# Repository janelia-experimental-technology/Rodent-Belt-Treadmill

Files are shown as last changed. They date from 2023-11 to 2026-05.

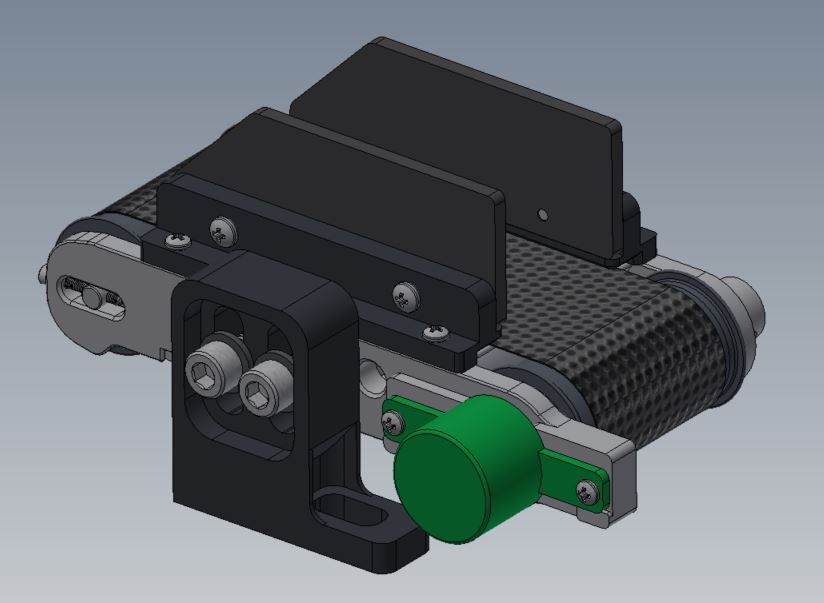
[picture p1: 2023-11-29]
J005558 TREADMILL.JPG

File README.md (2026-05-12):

# Rodent-Belt-Treadmill
Low friction belt treadmill for use in space constrained experimental rigs

Designed at HHMI's Janelia research campus by the jET team, this treadmill is relatively small and inexpensive compared to most existing designs. It is manually driven with an encoder which tracks the movement of the belt. The encoder does not have to be connected, unless it is desired to record or analyze the motion. Encoder interfaces are documented in a separate repository here: https://github.com/janelia-experimental-technology/Treadmill-Interface as the interface may be used with multiple treadmill types.

It may be used for natural action (e.g., walking) for the mouse to take during an experiment instead of standing still. For example, some users let the mice walk normally on the treadmill and then play a tone the mouse associates with a trained response to see if the mouse will start or stop moving.

Advantages: This was designed to fit underneath MIMMS 2P microscopes where space is limited. There are now some commercial options available based on this design, as well as other commercial options.

Interface: These may be placed under an imaging microscope or other behavioral setup with a head-fixed rodent on it. 

Construction: The treadmill is composed of 3D printed parts and two machined axles that can be made by a machine shop on a lathe with simple tooling. There are also some laser cut side walls on the treadmill and a laser cut belt as well. 
The belt is seamed together using a heat sealer such as this one from Amazon: 
8" (200mm) Impulse Manual Bag Sealer Heat Sealer http://a.co/8Zj5Gaq

Teflon tape used to hold the belt halves in position:
http://catalog.cshyde.com/keyword/s-ptfe-teflon-products-ptfe-teflon-tapes-4/skived-high-density-ptfe-tape-with-silicone?key=all&&keyword=R233&SchType=2

See the individual part drawings for more detail on printing and fabricating each parts. See the attached assembly drawing for the BOM including purchased commercial items needed to complete the treadmill. 

Operation: Researchers can physically mount the treadmill and place the mouse on top of it. Some training is required of the mouse. 

Maintenance: The belts need to be cleaned regularly to keep them turning smoothly. Many users have spare belts that they swap between. If there is enough space in your rig other options such as the cylindrical treadmill are good options that do not require as much maintenance. 

Opportunity: Free to make for Non-Profit Research by downloading the design here or on Flintbox. See included hardware license. 

Rights and designs available for Commercial License. Janelia makes no endorsements or guarantees of licensee products.

For inquiries, please contact innovation@janelia.hhmi.org and reference: Janelia 2017-049
https://hhmi.flintbox.com/technologies/5e4af2a5-6154-4bc0-a10d-56b5b6dce978

To cite the designs, please use DOI:  https://doi.org/10.25378/janelia.24691311

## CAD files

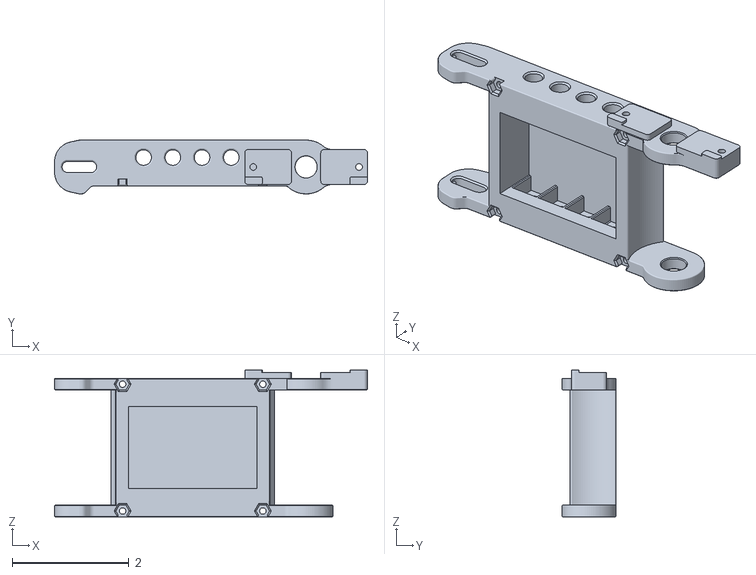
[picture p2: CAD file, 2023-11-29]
Part Models and Drawings/J007811 NRB MAIN BODY INSERTS Rev -.stl
5.35 x 0.922 x 2.51

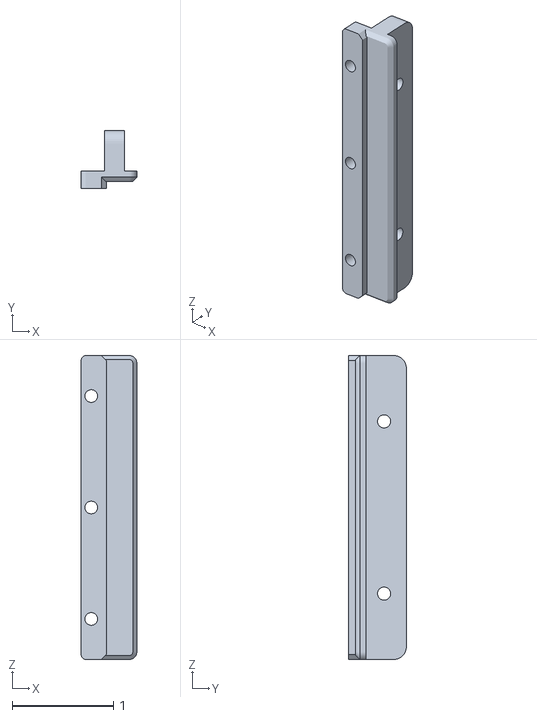
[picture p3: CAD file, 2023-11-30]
Part Models and Drawings/J006163 NRB LOW GUIDE RAIL Rev -.stl
0.55 x 0.57 x 3.00

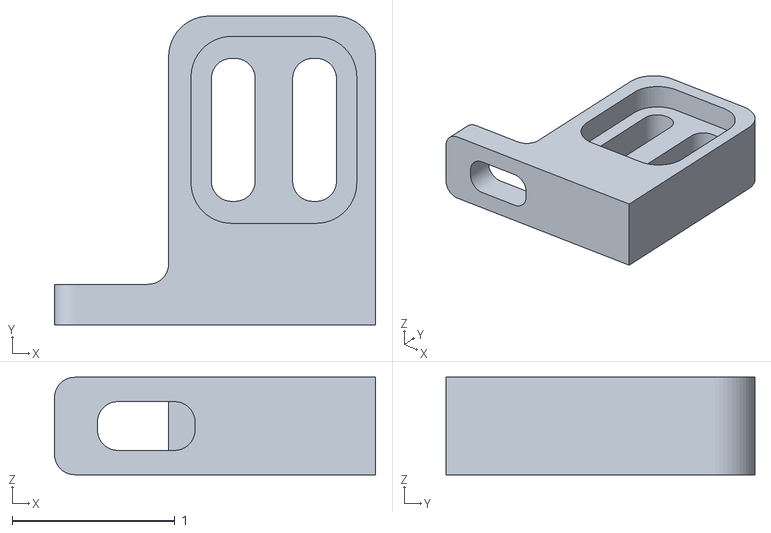
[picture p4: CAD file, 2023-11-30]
Part Models and Drawings/J005557 NRB ADJ BRKT MR Rev -.stl
1.98 x 1.90 x 0.6

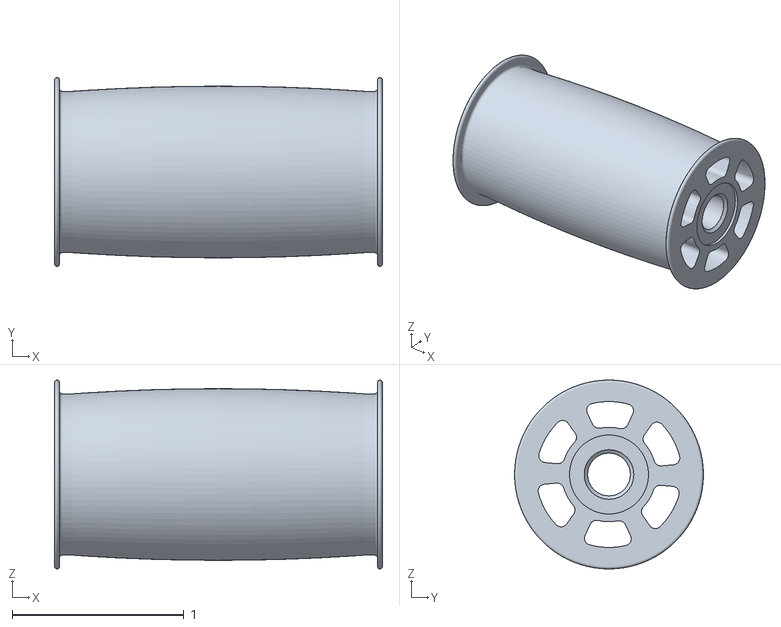
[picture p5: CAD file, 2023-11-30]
Part Models and Drawings/J005553 NRB DRIVE ROLLER Rev -.stl
1.91 x 1.10 x 1.10

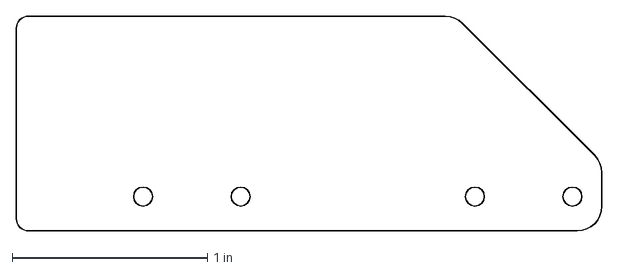
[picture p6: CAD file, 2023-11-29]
Part Models and Drawings/J005548 NRB BRKT SIDE WALL Rev A.dxf
3.00 x 1.10 in

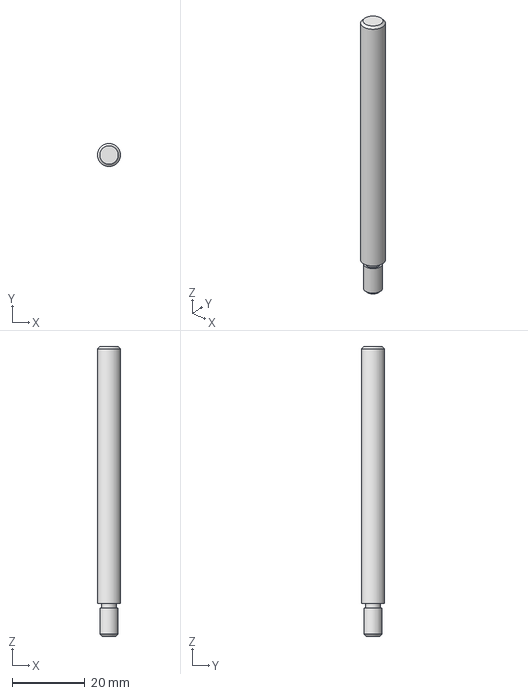
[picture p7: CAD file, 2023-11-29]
Part Models and Drawings/J005526 NRB DRIVE SHAFT Rev A.stp
6.34 x 6.35 x 79.7 mm

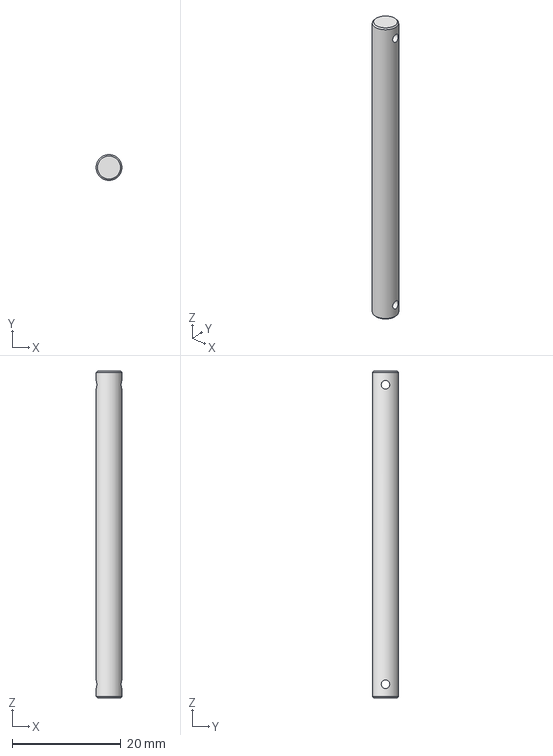
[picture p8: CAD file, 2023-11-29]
Part Models and Drawings/J005527 NRB IDLER SHAFT Rev A.stp
4.75 x 4.75 x 60.2 mm

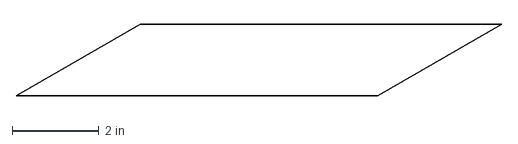
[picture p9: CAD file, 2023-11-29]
Part Models and Drawings/J005559 NRB BELT FLAT PATTERN Rev B.dxf
11.2 x 1.65 in

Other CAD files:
Part Models and Drawings/J005556 NRB ADJ BRKT ML Rev -.stl
Part Models and Drawings/J005551 NRB ROLLER Rev -.stl
Pack and Go Inventor Files/57155K335.ipt
Pack and Go Inventor Files/57155K336.ipt
Pack and Go Inventor Files/90107A126.ipt
Pack and Go Inventor Files/90965A170.ipt
Pack and Go Inventor Files/91828A113_TYPE 18-8 STAINLESS STEEL HEX NUT.ipt
Pack and Go Inventor Files/92000A106.ipt
Pack and Go Inventor Files/92000A112.ipt
Pack and Go Inventor Files/92000A118.ipt
Pack and Go Inventor Files/92196A540.ipt
Pack and Go Inventor Files/92290A746.ipt
Pack and Go Inventor Files/94785A415_TYPE 18-8 STAINLESS STEEL SQUARE NUT.ipt
Pack and Go Inventor Files/98317A214.ipt
Pack and Go Inventor Files/9946K110.ipt
Pack and Go Inventor Files/HEDR-5420-ES214.ipt
Pack and Go Inventor Files/HEDR-5420-ES214_DISC.ipt
Pack and Go Inventor Files/NRB ADJ BRKT ML.ipt
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

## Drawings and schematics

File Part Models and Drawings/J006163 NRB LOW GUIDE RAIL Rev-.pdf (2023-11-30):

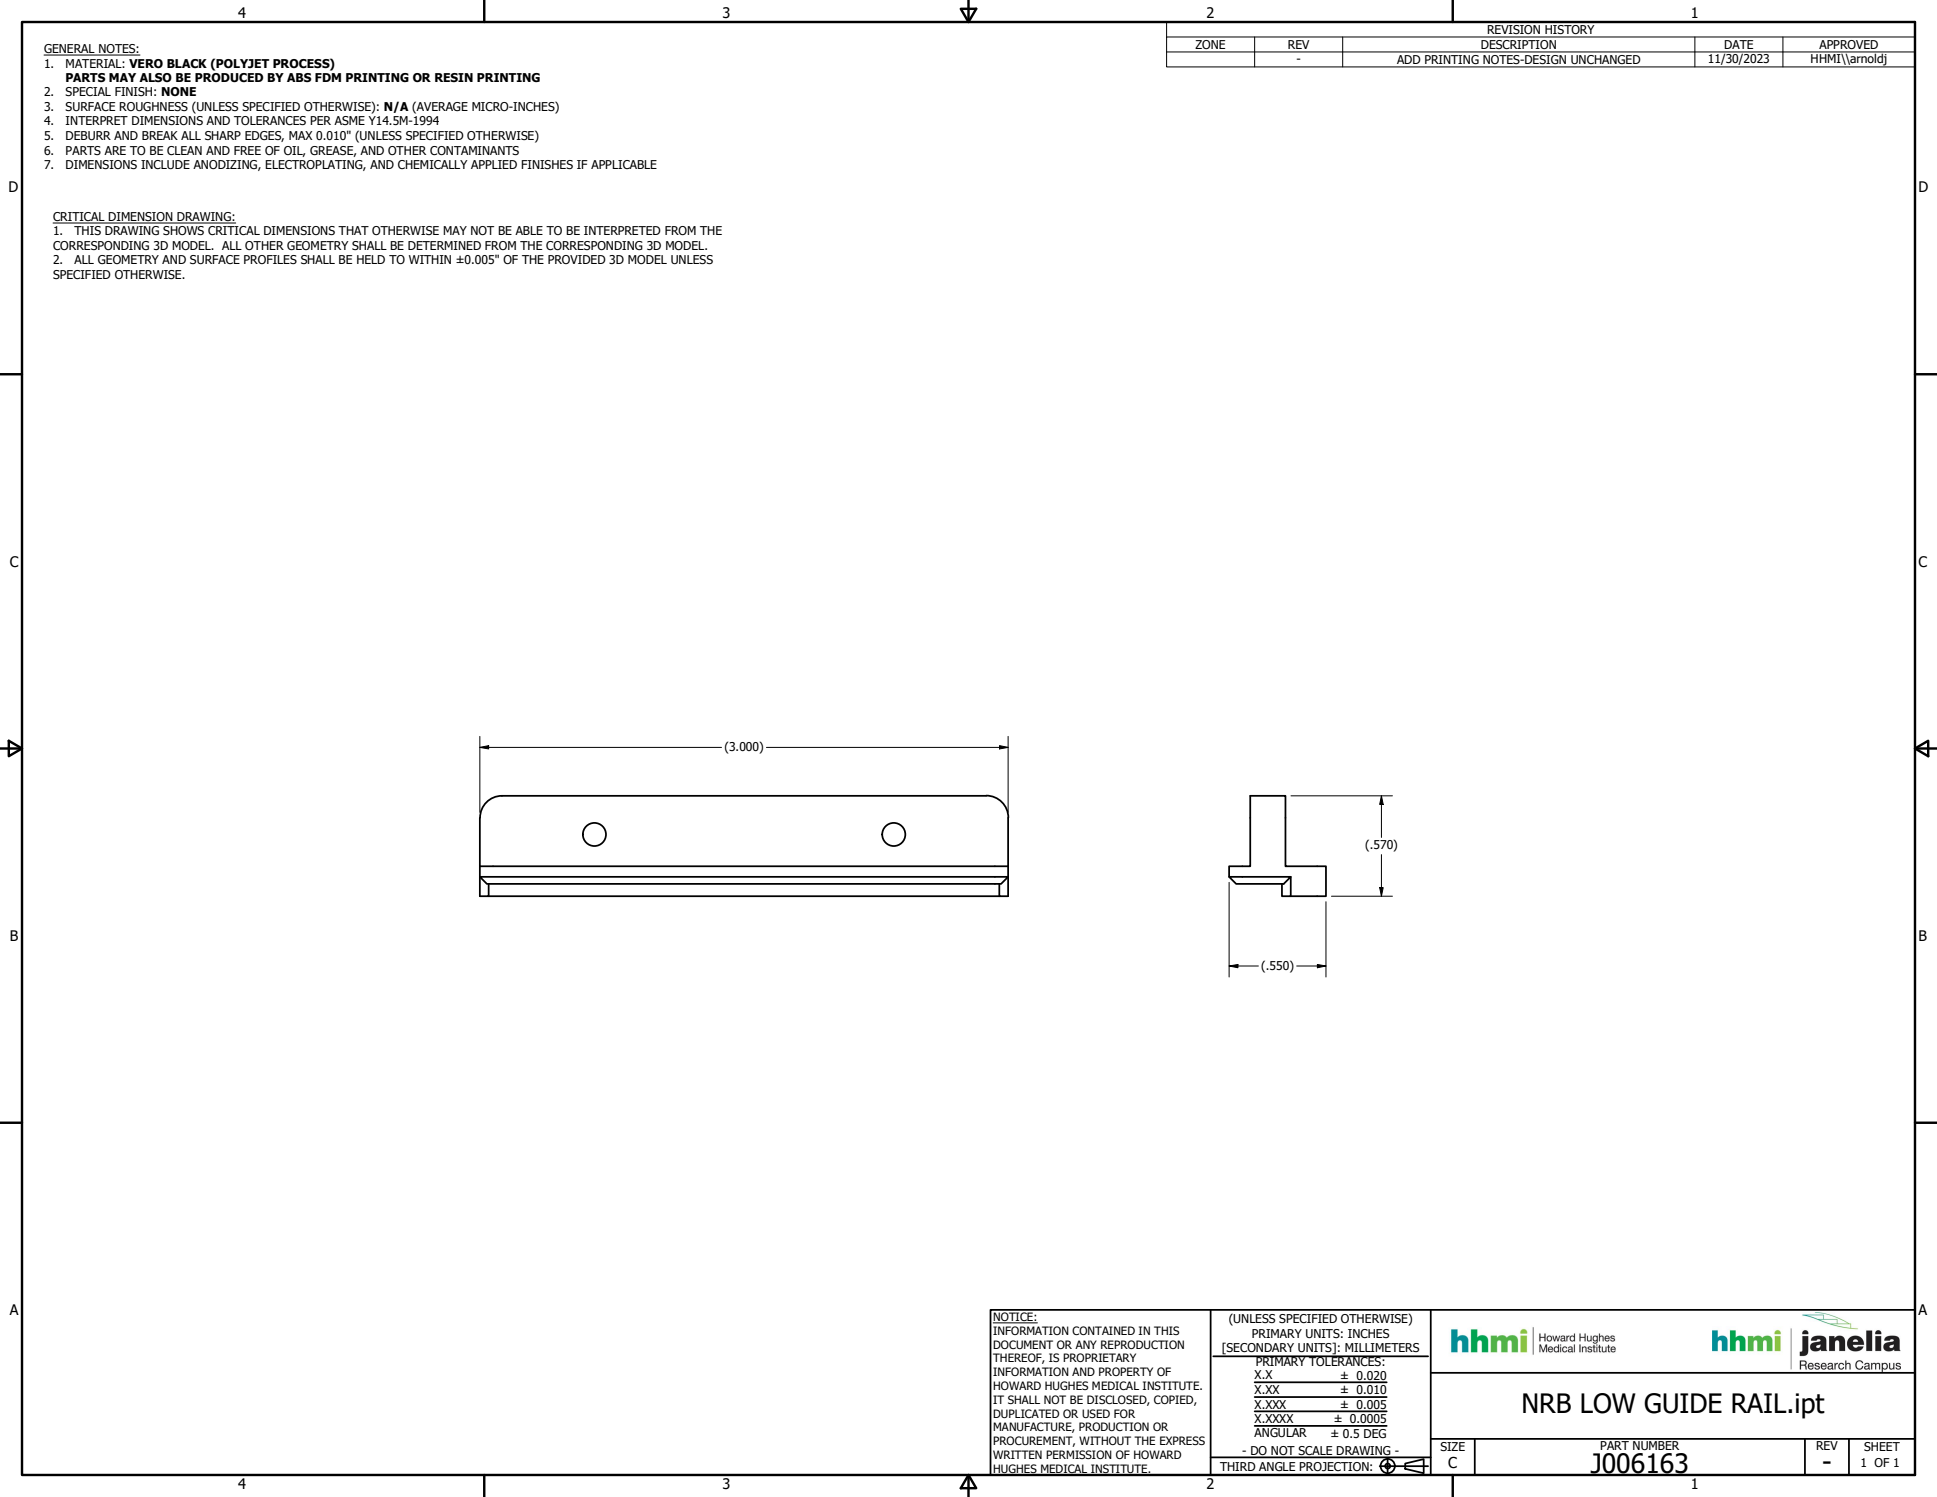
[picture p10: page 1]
PART NUMBER; 1 OF 1 THIRD ANGLE PROJECTION:; ± 0.020 ± 0.010 ± 0.005 ± 0.0005 ± 0.5 DEG; REVISION HISTORY

GENERAL NOTES:
1. MATERIAL: VERO BLACK (POLYJET PROCESS)
PARTS MAY ALSO BE PRODUCED BY ABS FDM PRINTING OR RESIN PRINTING
2. SPECIAL FINISH: NONE
3. SURFACE ROUGHNESS (UNLESS SPECIFIED OTHERWISE): N/A (AVERAGE MICRO-INCHES)
4. INTERPRET DIMENSIONS AND TOLERANCES PER ASME Y14.5M-1994
5. DEBURR AND BREAK ALL SHARP EDGES, MAX 0.010" (UNLESS SPECIFIED OTHERWISE)
6. PARTS ARE TO BE CLEAN AND FREE OF OIL, GREASE, AND OTHER CONTAMINANTS
7. DIMENSIONS INCLUDE ANODIZING, ELECTROPLATING, AND CHEMICALLY APPLIED FINISHES IF APPLICABLE

ZONE | REV | DESCRIPTION | DATE | APPROVED

- | ADD PRINTING NOTES-DESIGN UNCHANGED | 11/30/2023 | HHMI\\arnoldj

CRITICAL DIMENSION DRAWING:
1. THIS DRAWING SHOWS CRITICAL DIMENSIONS THAT OTHERWISE MAY NOT BE ABLE TO BE INTERPRETED FROM THE
CORRESPONDING 3D MODEL. ALL OTHER GEOMETRY SHALL BE DETERMINED FROM THE CORRESPONDING 3D MODEL.
2. ALL GEOMETRY AND SURFACE PROFILES SHALL BE HELD TO WITHIN ±0.005" OF THE PROVIDED 3D MODEL UNLESS
SPECIFIED OTHERWISE.

NOTICE:
INFORMATION CONTAINED IN THIS
DOCUMENT OR ANY REPRODUCTION
THEREOF, IS PROPRIETARY
INFORMATION AND PROPERTY OF
HOWARD HUGHES MEDICAL INSTITUTE.
IT SHALL NOT BE DISCLOSED, COPIED,
DUPLICATED OR USED FOR
MANUFACTURE, PRODUCTION OR
PROCUREMENT, WITHOUT THE EXPRESS
WRITTEN PERMISSION OF HOWARD
HUGHES MEDICAL INSTITUTE.

(UNLESS SPECIFIED OTHERWISE)
PRIMARY UNITS: INCHES
[SECONDARY UNITS]: MILLIMETERS
PRIMARY TOLERANCES:
X.XXX
X.XXXX
ANGULAR
- DO NOT SCALE DRAWING -

NRB LOW GUIDE RAIL.ipt

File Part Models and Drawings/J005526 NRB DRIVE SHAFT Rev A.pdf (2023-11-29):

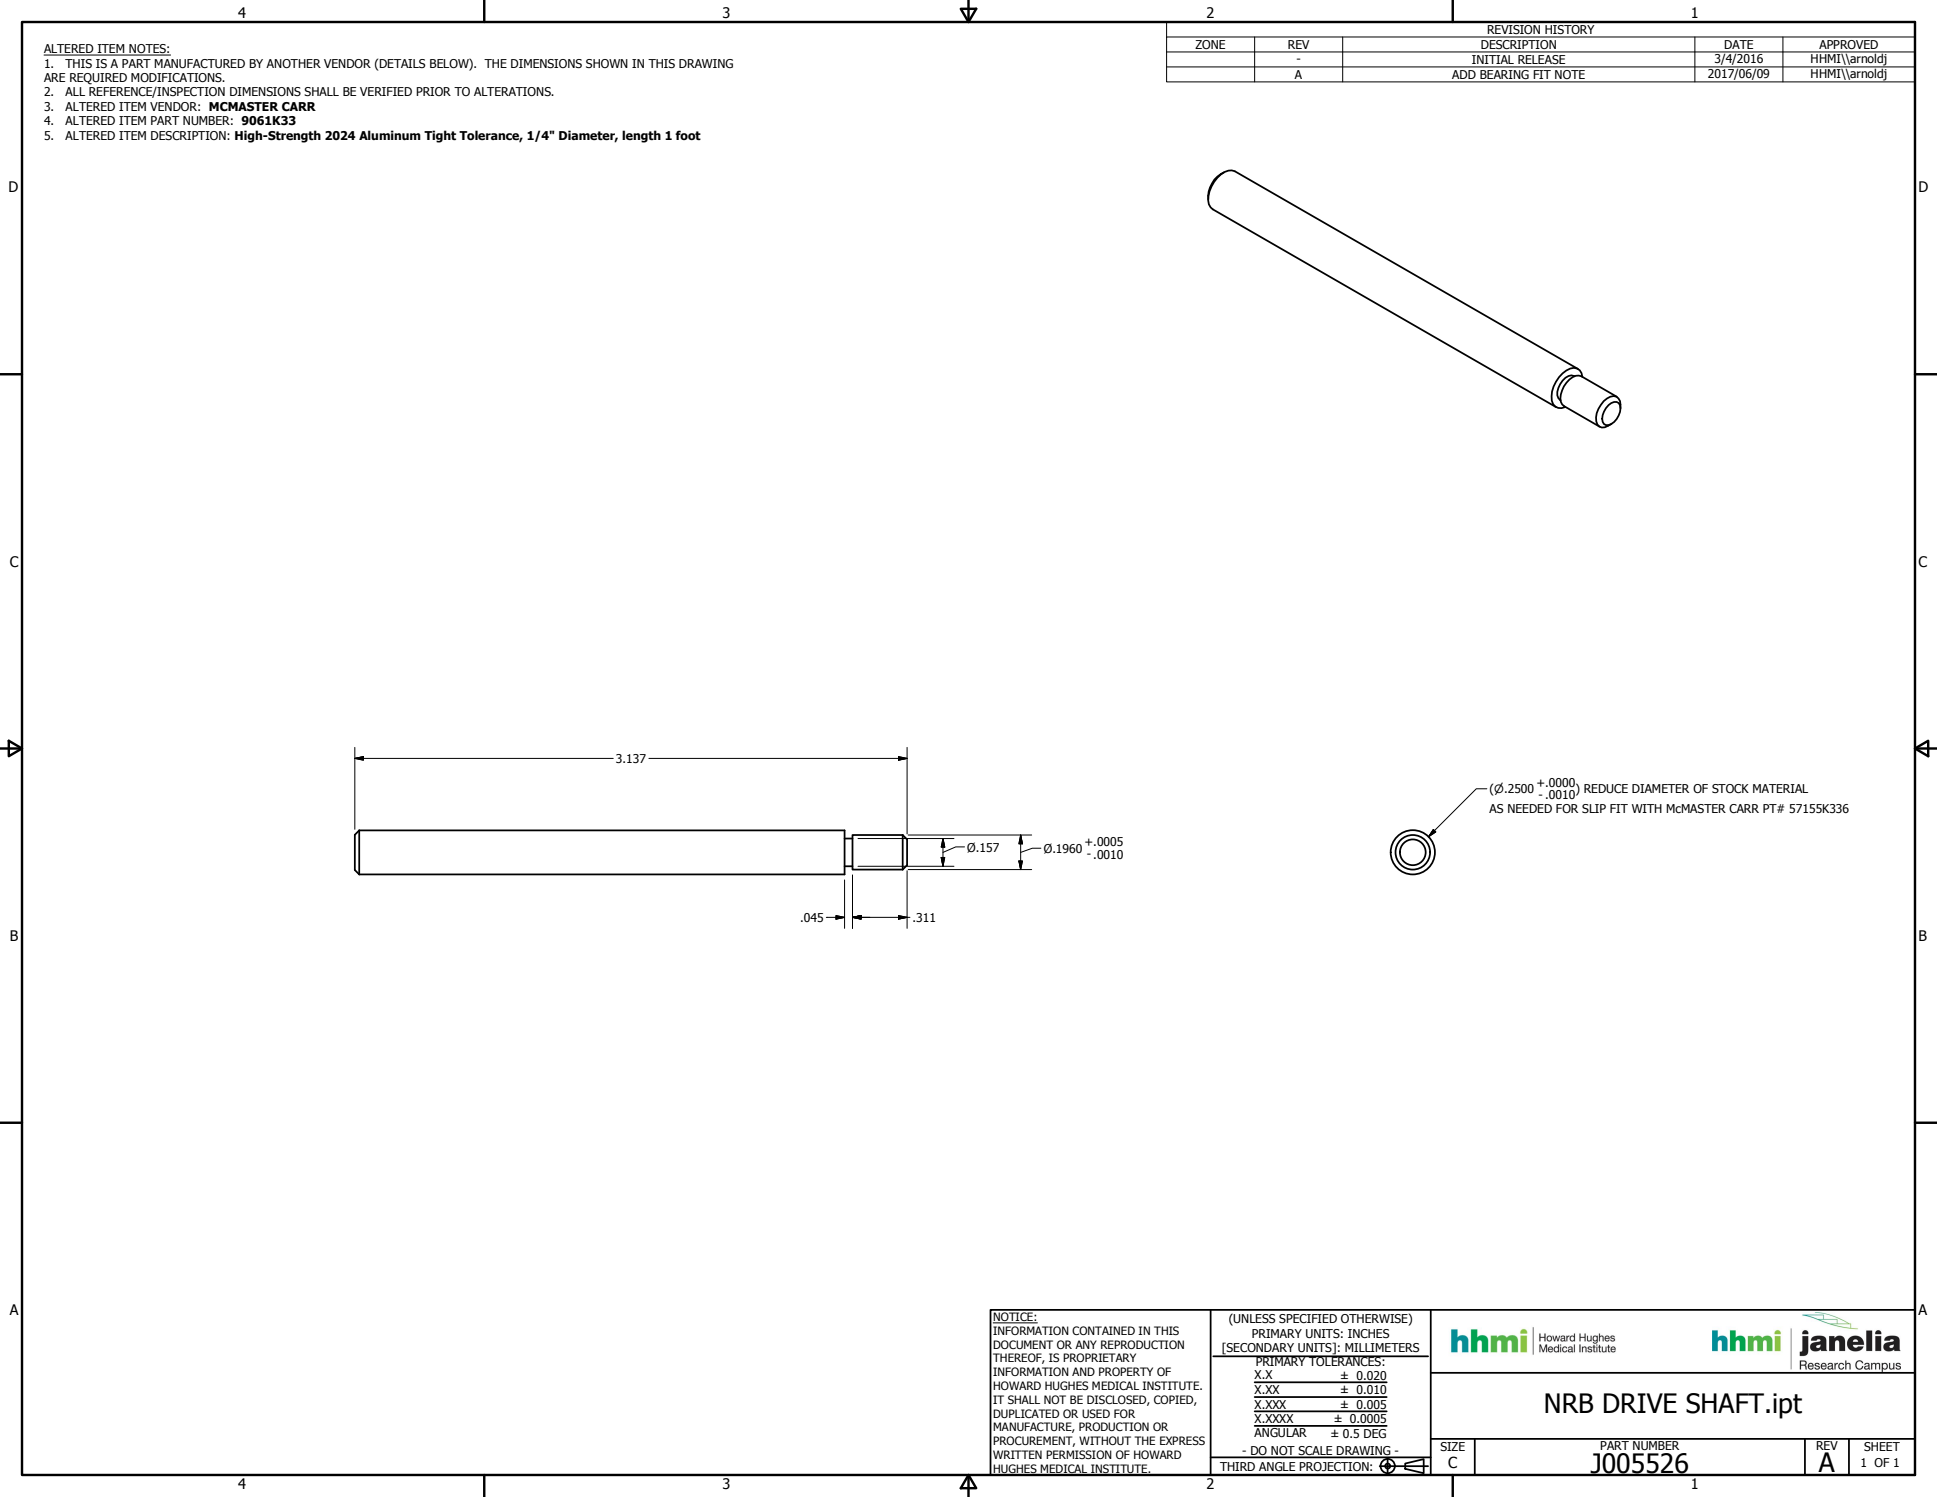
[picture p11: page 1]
PART NUMBER; SIZE; REV; SHEET; 1 OF 1 THIRD ANGLE PROJECTION:; ± 0.020 ± 0.010 ± 0.005 ± 0.0005 ± 0.5 DEG; REVISION HISTORY; ZONE; DESCRIPTION; DATE; APPROVED; INITIAL RELEASE; HHMI\\arnoldj; ADD BEARING FIT NOTE; ) REDUCE DIAMETER OF STOCK MATERIAL

ALTERED ITEM NOTES:
1. THIS IS A PART MANUFACTURED BY ANOTHER VENDOR (DETAILS BELOW). THE DIMENSIONS SHOWN IN THIS DRAWING
ARE REQUIRED MODIFICATIONS.
2. ALL REFERENCE/INSPECTION DIMENSIONS SHALL BE VERIFIED PRIOR TO ALTERATIONS.
3. ALTERED ITEM VENDOR: MCMASTER CARR
4. ALTERED ITEM PART NUMBER: 9061K33
5. ALTERED ITEM DESCRIPTION: High-Strength 2024 Aluminum Tight Tolerance, 1/4" Diameter, length 1 foot

AS NEEDED FOR SLIP FIT WITH McMASTER CARR PT# 57155K336

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

NRB DRIVE SHAFT.ipt

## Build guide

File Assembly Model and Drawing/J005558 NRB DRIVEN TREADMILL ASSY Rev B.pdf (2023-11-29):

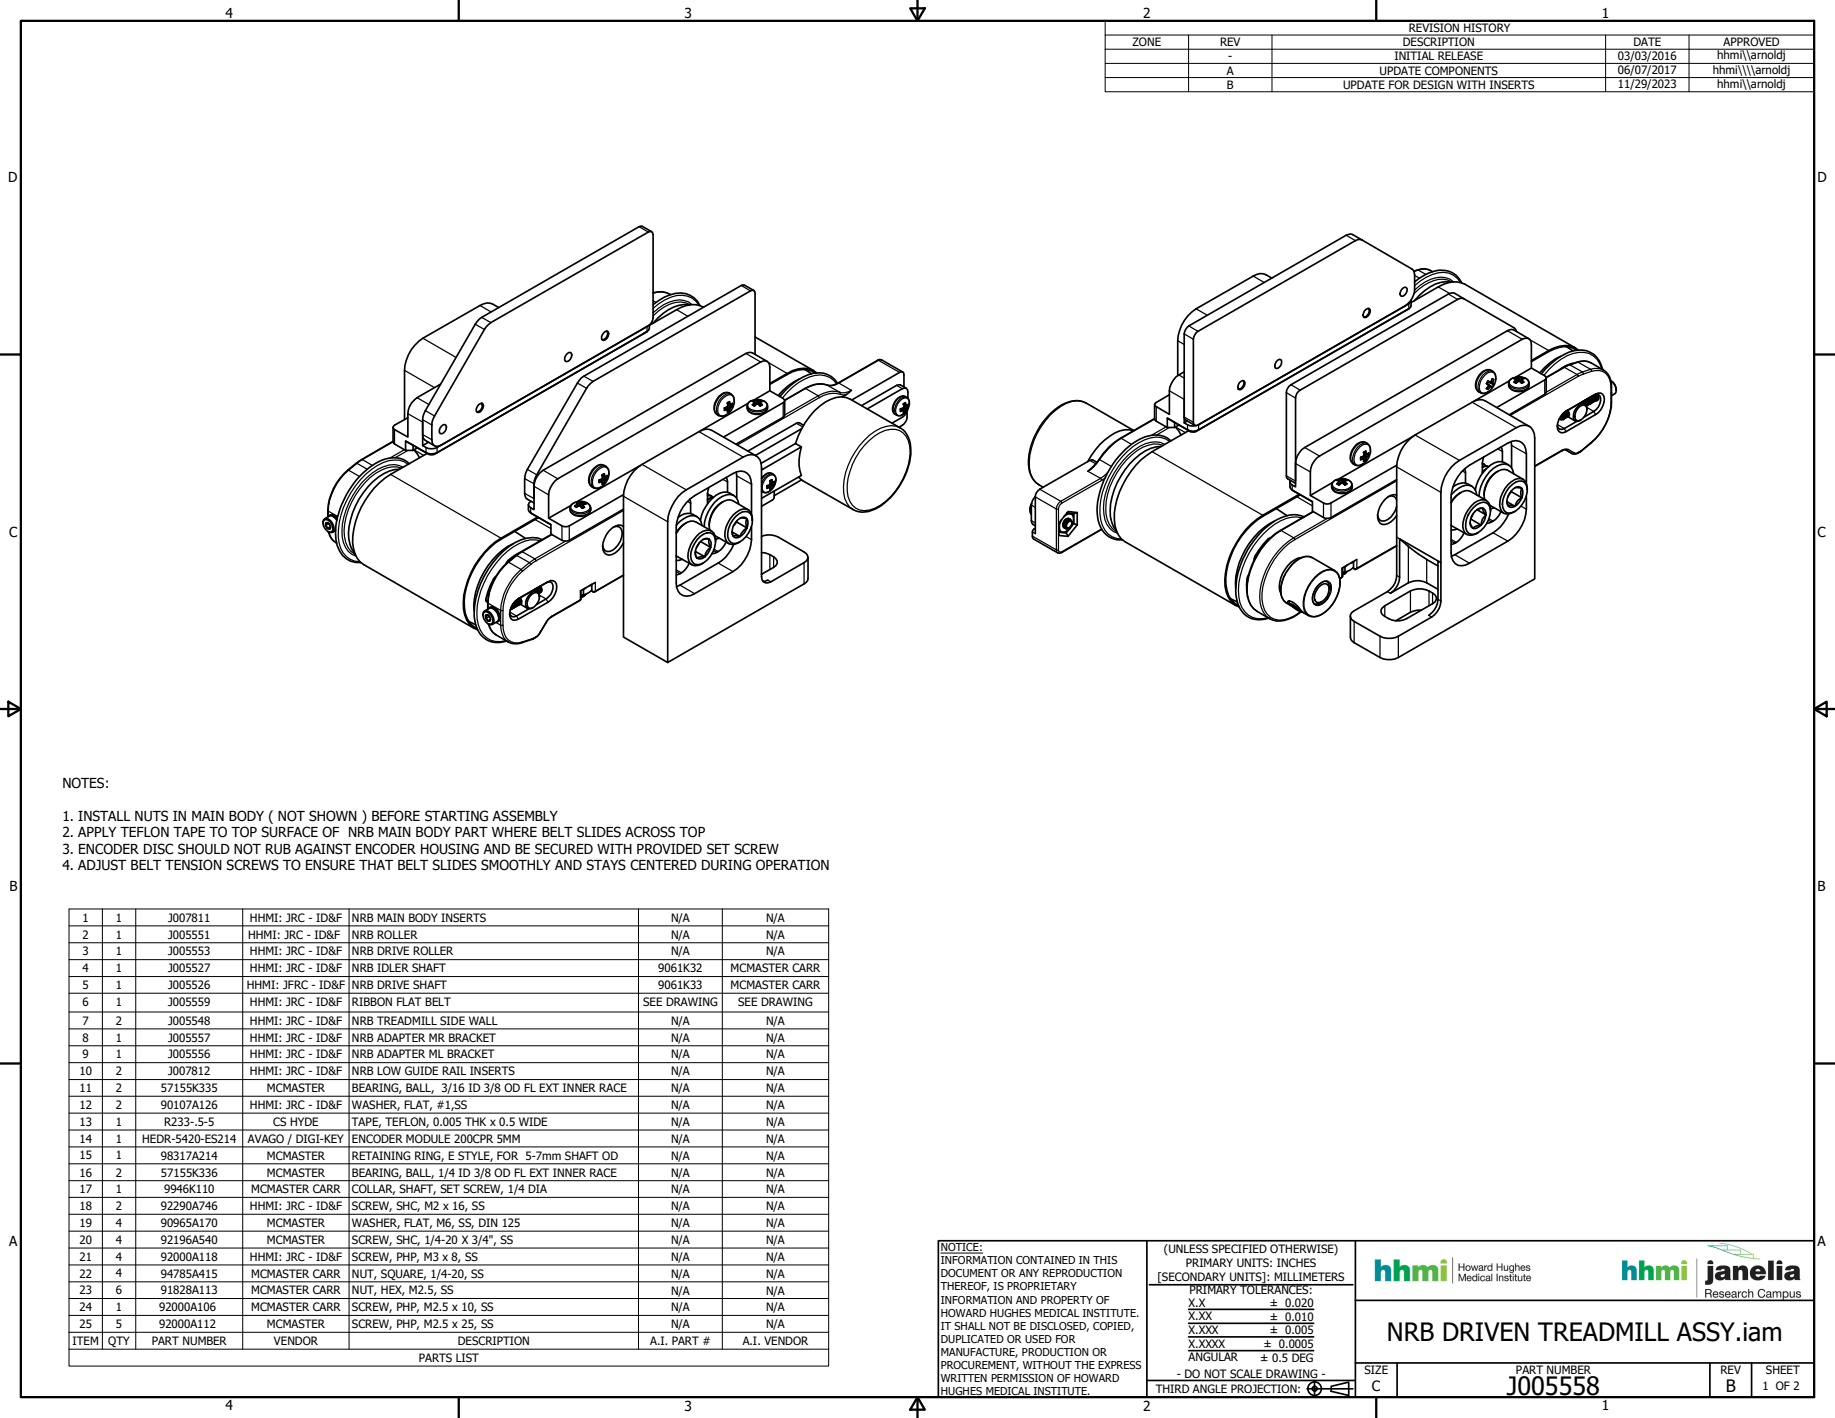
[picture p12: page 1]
MCMASTER CARR; SCREW, PHP, M2.5 x 10, SS; PARTS LIST; PART NUMBER; 1 OF 2 THIRD ANGLE PROJECTION:; - DO NOT SCALE DRAWING -; ± 0.020 ± 0.010 ± 0.005 ± 0.0005 ± 0.5 DEG; PRIMARY TOLERANCES:; REVISION HISTORY

ZONE | REV | DESCRIPTION | DATE | APPROVED

- | INITIAL RELEASE | 03/03/2016 | hhmi\\arnoldj
A | UPDATE COMPONENTS | 06/07/2017 | hhmi\\\\arnoldj
B | UPDATE FOR DESIGN WITH INSERTS | 11/29/2023 | hhmi\\arnoldj

1. INSTALL NUTS IN MAIN BODY ( NOT SHOWN ) BEFORE STARTING ASSEMBLY
2. APPLY TEFLON TAPE TO TOP SURFACE OF NRB MAIN BODY PART WHERE BELT SLIDES ACROSS TOP
3. ENCODER DISC SHOULD NOT RUB AGAINST ENCODER HOUSING AND BE SECURED WITH PROVIDED SET SCREW
4. ADJUST BELT TENSION SCREWS TO ENSURE THAT BELT SLIDES SMOOTHLY AND STAYS CENTERED DURING OPERATION

1 | 1 | J007811 | HHMI: JRC - ID&F | NRB MAIN BODY INSERTS | N/A | N/A
2 | 1 | J005551 | HHMI: JRC - ID&F | NRB ROLLER | N/A | N/A
3 | 1 | J005553 | HHMI: JRC - ID&F | NRB DRIVE ROLLER | N/A | N/A
4 | 1 | J005527 | HHMI: JRC - ID&F | NRB IDLER SHAFT | 9061K32 | MCMASTER CARR
5 | 1 | J005526 | HHMI: JFRC - ID&F | NRB DRIVE SHAFT | 9061K33 | MCMASTER CARR
6 | 1 | J005559 | HHMI: JRC - ID&F | RIBBON FLAT BELT | SEE DRAWING | SEE DRAWING
7 | 2 | J005548 | HHMI: JRC - ID&F | NRB TREADMILL SIDE WALL | N/A | N/A
8 | 1 | J005557 | HHMI: JRC - ID&F | NRB ADAPTER MR BRACKET | N/A | N/A
9 | 1 | J005556 | HHMI: JRC - ID&F | NRB ADAPTER ML BRACKET | N/A | N/A
10 | 2 | J007812 | HHMI: JRC - ID&F | NRB LOW GUIDE RAIL INSERTS | N/A | N/A
11 | 2 | 57155K335 | MCMASTER | BEARING, BALL, 3/16 ID 3/8 OD FL EXT INNER RACE | N/A | N/A
12 | 2 | 90107A126 | HHMI: JRC - ID&F | WASHER, FLAT, #1,SS | N/A | N/A
13 | 1 | R233-.5-5 | CS HYDE | TAPE, TEFLON, 0.005 THK x 0.5 WIDE | N/A | N/A
14 | 1 | HEDR-5420-ES214 | AVAGO / DIGI-KEY | ENCODER MODULE 200CPR 5MM | N/A | N/A
15 | 1 | 98317A214 | MCMASTER | RETAINING RING, E STYLE, FOR 5-7mm SHAFT OD | N/A | N/A
16 | 2 | 57155K336 | MCMASTER | BEARING, BALL, 1/4 ID 3/8 OD FL EXT INNER RACE | N/A | N/A
17 | 1 | 9946K110 | MCMASTER CARR | COLLAR, SHAFT, SET SCREW, 1/4 DIA | N/A | N/A
18 | 2 | 92290A746 | HHMI: JRC - ID&F | SCREW, SHC, M2 x 16, SS | N/A | N/A
19 | 4 | 90965A170 | MCMASTER | WASHER, FLAT, M6, SS, DIN 125 | N/A | N/A
20 | 4 | 92196A540 | MCMASTER | SCREW, SHC, 1/4-20 X 3/4", SS | N/A | N/A
21 | 4 | 92000A118 | HHMI: JRC - ID&F | SCREW, PHP, M3 x 8, SS | N/A | N/A
22 | 4 | 94785A415 | MCMASTER CARR | NUT, SQUARE, 1/4-20, SS | N/A | N/A
23 | 6 | 91828A113 | MCMASTER CARR | NUT, HEX, M2.5, SS | N/A | N/A

NOTICE: INFORMATION CONTAINED IN THIS DOCUMENT OR ANY REPRODUCTION THEREOF, IS PROPRIETARY INFORMATION AND PROPERTY OF HOWARD HUGHES MEDICAL INSTITUTE. IT SHALL NOT BE DISCLOSED, COPIED, DUPLICATED OR USED FOR MANUFACTURE, PRODUCTION OR PROCUREMENT, WITHOUT THE EXPRESS WRITTEN PERMISSION OF HOWARD HUGHES MEDICAL INSTITUTE. | (UNLESS SPECIFIED OTHERWISE) PRIMARY UNITS: INCHES [SECONDARY UNITS]: MILLIMETERS

25 | 5 | 92000A112 | MCMASTER | SCREW, PHP, M2.5 x 25, SS | N/A | N/A
ITEM | QTY | PART NUMBER | VENDOR | DESCRIPTION | A.I. PART # | A.I. VENDOR

NRB DRIVEN TREADMILL ASSY.iam

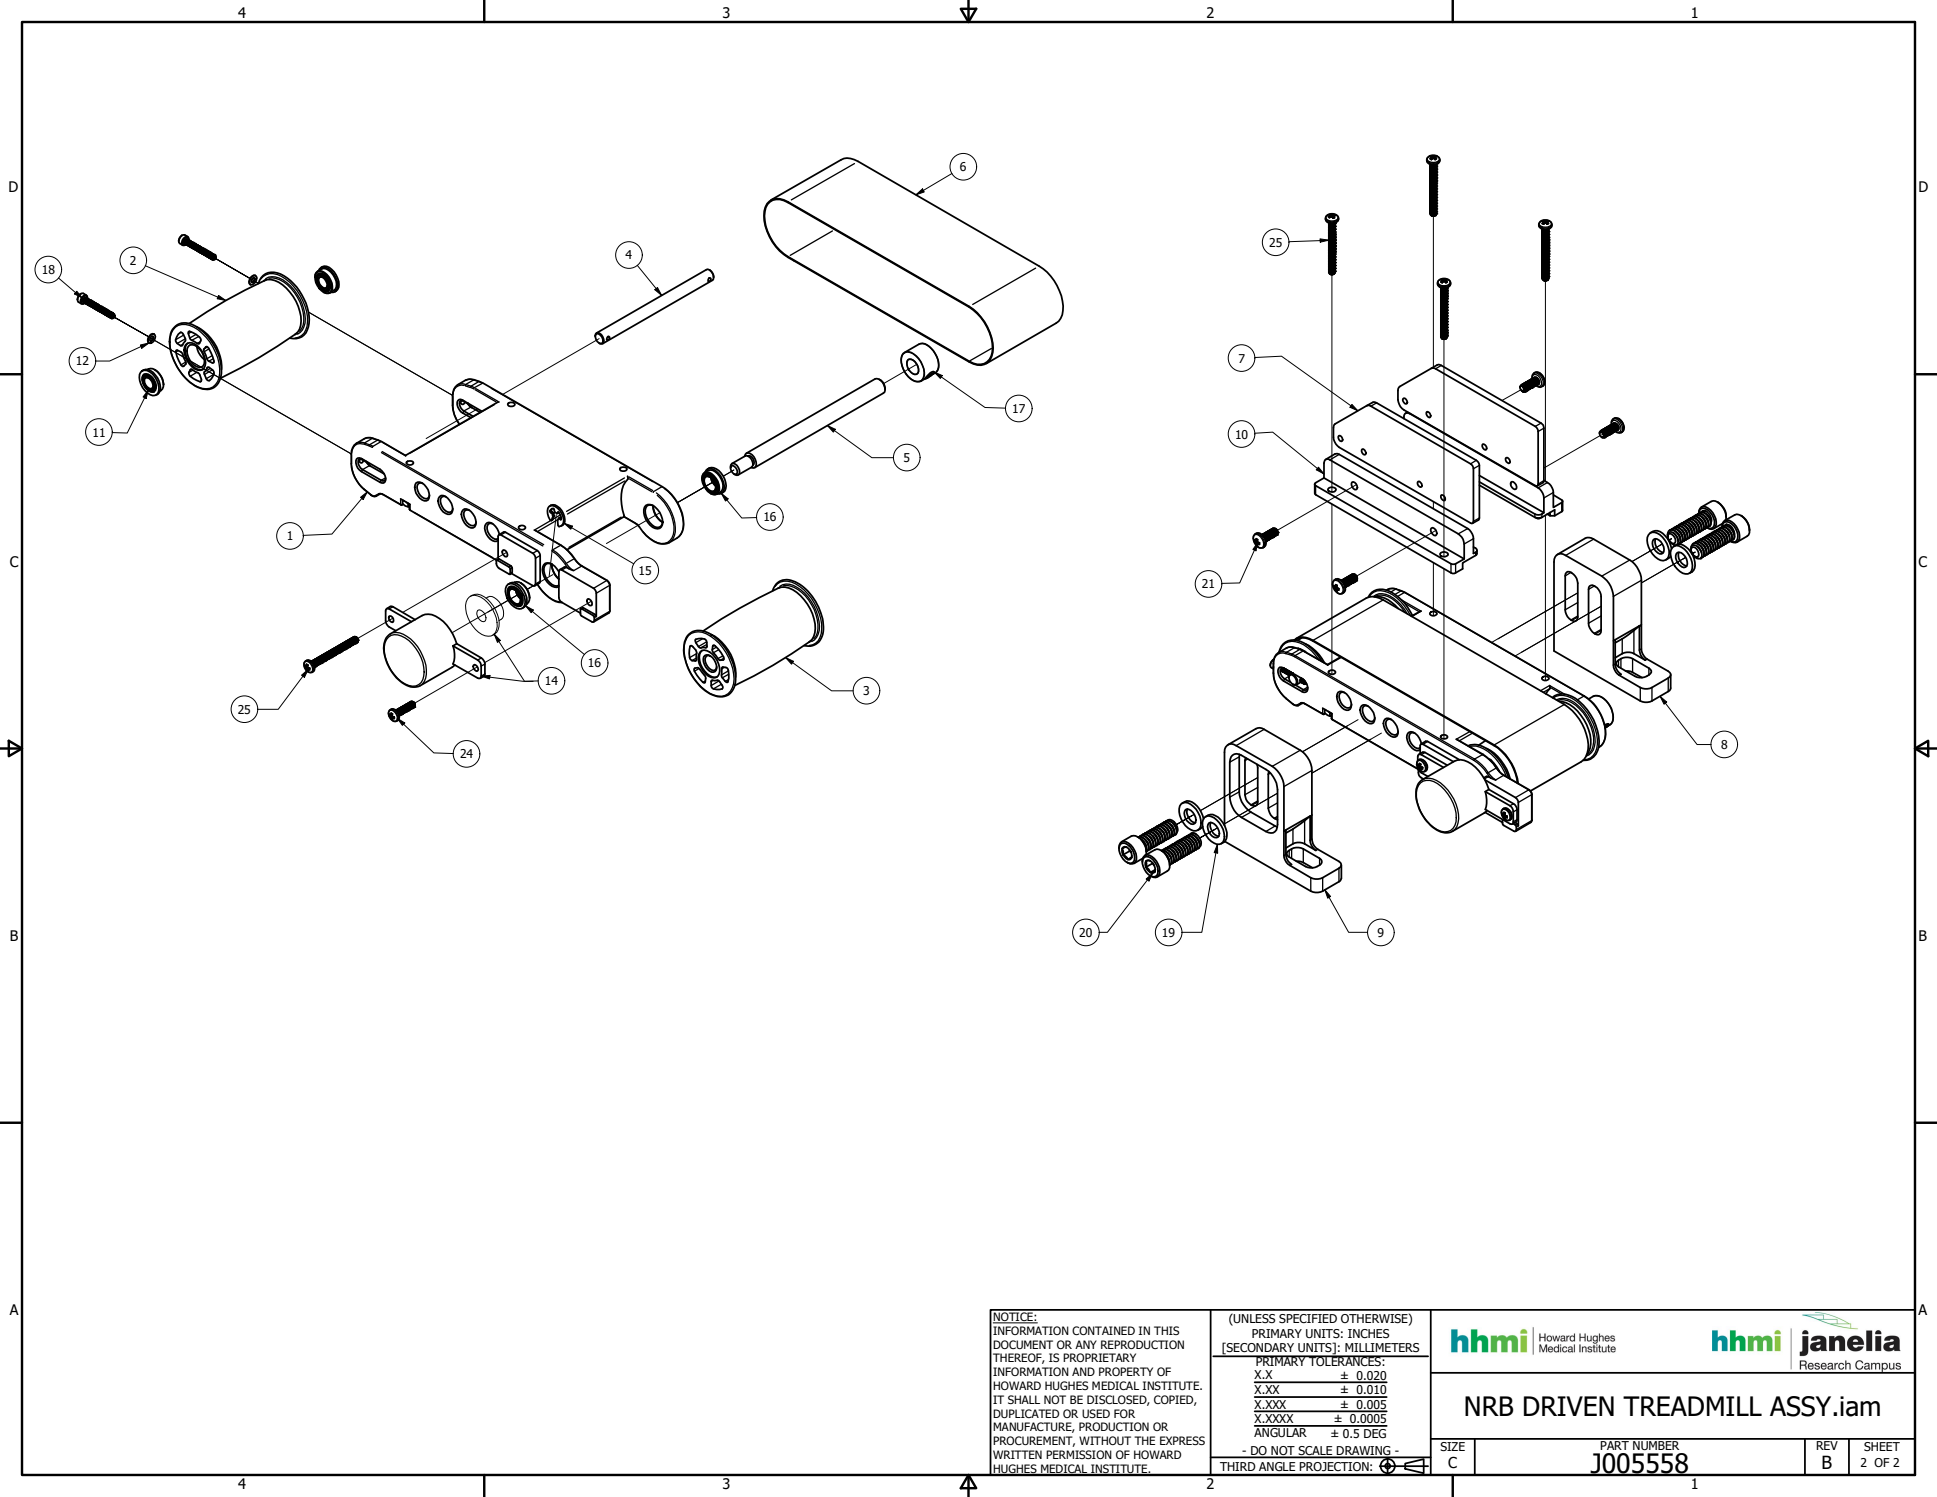
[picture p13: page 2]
PART NUMBER; 2 OF 2 THIRD ANGLE PROJECTION:; ± 0.020 ± 0.010 ± 0.005 ± 0.0005 ± 0.5 DEG

NOTICE:
INFORMATION CONTAINED IN THIS
DOCUMENT OR ANY REPRODUCTION
THEREOF, IS PROPRIETARY
INFORMATION AND PROPERTY OF
HOWARD HUGHES MEDICAL INSTITUTE.
IT SHALL NOT BE DISCLOSED, COPIED,
DUPLICATED OR USED FOR
MANUFACTURE, PRODUCTION OR
PROCUREMENT, WITHOUT THE EXPRESS
WRITTEN PERMISSION OF HOWARD
HUGHES MEDICAL INSTITUTE.

(UNLESS SPECIFIED OTHERWISE)
PRIMARY UNITS: INCHES
[SECONDARY UNITS]: MILLIMETERS
PRIMARY TOLERANCES:
X.XXX
X.XXXX
ANGULAR
- DO NOT SCALE DRAWING -

NRB DRIVEN TREADMILL ASSY.iam
